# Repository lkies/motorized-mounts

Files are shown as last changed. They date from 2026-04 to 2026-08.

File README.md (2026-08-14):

# DIY Motorized Mirror Mounts

_Lorenz Kies <[lorenz.kies@aei.uni-hannover.de](mailto:lorenz.kies@aei.uni-hannover.de)>_

_I designed this project during my employment as a research assistant at the Institute of Gravitational Physics at Leibniz University Hannover; it is therefore intellectual property of my employer, but I have been given permission to share it under an open source license._

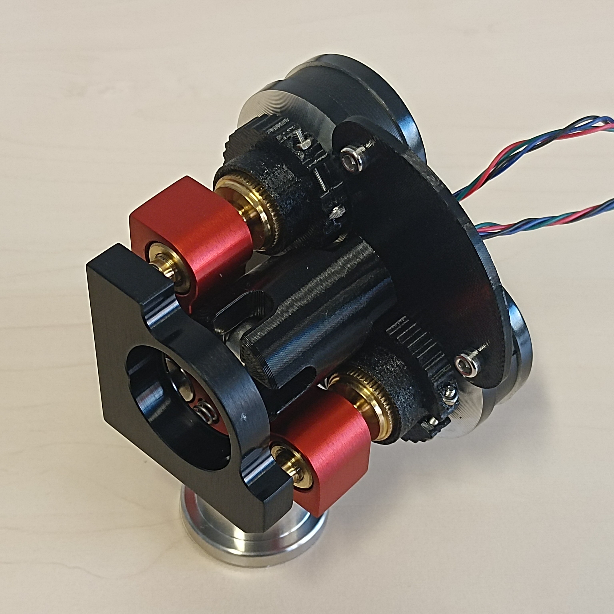
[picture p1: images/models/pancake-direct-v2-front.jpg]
pancake-direct-v2 front view
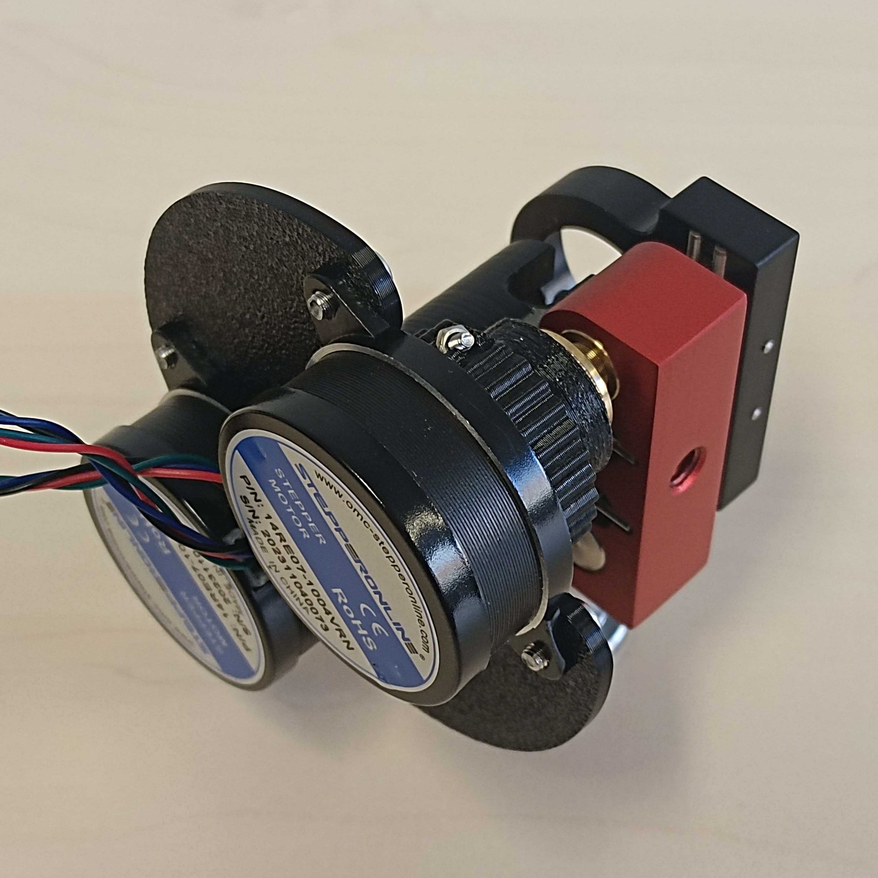
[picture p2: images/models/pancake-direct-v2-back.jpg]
pancake-direct-v2 back view
 

## Introduction

Motorized mirror mounts for guiding laser beams are already an established commercial product, but their pricing makes them unreasonable for basic automation tasks for most people. This means they are mostly reserved for applications where remote control or precise repeatable positioning is required. This is why I decided to develop a low-cost alternative for cheap automatic alignment of optical experiments. Most commercial offerings start at around $1000 per axis (including the driver), or around $4000 for a full 4-axis system required for most alignment problems. In contrast, my design can be build for under $100 for a full set, so less than $25 per axis, relying mostly on standard components and 3D printed parts. Despite the low cost, the actuator performance is competitive with lower-end commercial products and more than sufficient for most automatic alignment problems.

If you want to simply build the actuators, go to the [Instructions](#instructions) chapter. Following that, I discuss some of the [mechanical](#mechanical-design) and [electrical](#electrical-design) design considerations I made, that may be of interest to you, if you want to modify the designs. Finally, I discuss the [characterization](#characterization) experiments and metrics used to evaluate the performance of the actuators.

## Table of Contents

- [Introduction](#introduction)
- [Instructions](#instructions)
  - [Parts List](#parts-list)
  - [Actuator Assembly Instructions](#actuator-assembly-instructions)
  - [Electronics Setup](#electronics-setup)
  - [Firmware Setup](#firmware-setup)
  - [API / Software Setup](#api--software-setup)
- [Design Considerations](#design-considerations)
  - [Mechanical Design](#mechanical-design)
  - [Backlash and Hysteresis Compensation](#backlash-and-hysteresis-compensation)
  - [Electrical Design](#electrical-design)
- [Characterization](#characterization)
  - [Minimal Incremental Motion](#minimal-incremental-motion)
  - [Unidirectional Repeatability](#unidirectional-repeatability)
  - [Nonlinearity](#nonlinearity)
  - [Backlash](#backlash)
  - [Backlash Variation](#backlash-variation)
  - [Interpretation](#interpretation)
  - [Results](#results)

## Instructions

These are the instructions to build the `pancake-direct-v2` design, which is the recommended design. The other designs are mostly included for completeness' sake, if you want to build them you will have to figure it out yourself from the CAD files.

### Parts List

To build a set of **four actuators** on two **mirrors**, you will need the following parts:

| Electronic Parts | Quantity |
| - | - |
| [NEMA 14 Pancake Stepper Motor](https://www.omc-stepperonline.com/de/e-serie-runden-nema-14-bipolar-0-9deg-8ncm-11-33oz-in-1-0a-36x17mm-4-draehte-14re07-1004vrn) | 4 |
| [TMC2208 StepStick V1.2](https://aliexpress.com/item/33045459259.html) | 4 |
| [Makerbase MKS DLC32 MAX](https://aliexpress.com/item/1005008204547315.html) | 1 |
| [19V 5A Power Supply (5.5mm x 2.5mm socket)](https://de.rs-online.com/web/p/steckernetzteile/2552119) | 1 |
| [Cat7 U/FTP 2m Ethernet Cable](https://de.rs-online.com/web/p/ethernetkabel/2660713) (optional) | 2 |
| [Adapter-Board-Stepper](electrical/adapter-board-stepper) (optional) | 2 |
| [Adapter-Board-Controller](electrical/adapter-board-controller) (optional) | 2 |
| [RJ45 Socket](https://de.rs-online.com/web/p/ethernet-steckverbinder/3316443?searchId=30a561ef-d51f-4305-b438-8268e3811f80) (optional, for adapter boards) | 4 |

The links for the motors, motor drivers, and driver board are not affiliate links, they are simply the first results I found. All parts are also offered by many other suppliers. If you can not find the exact same model, you should also be able to use similar parts that perform the same function.

There are a lot of other CNC driver boards out there, many of them ESP32 based. Alternatively, it is also not too difficult to build one yourself. Similarly, you can also use different stepper drivers like the TMC2209, DRV8825 or A4988. Most stepsticks are pin compatible at least to the extent required for basic operations. If you choose to buy TMC2208 stepsticks, I recommend getting the white v1.2 version, there are many step stick designs available and some of them seem to have weird factory side configurations. Although 15V and 3.5A should technically be enough for the power supply, I recommend staying on the safe side and getting a more powerful one like the one specified. If you do not have the capabilities to manufacture PCBs, you can also buy [RJ45](https://de.aliexpress.com/item/1005004520312413.html) breakout boards instead of the custom adapter boards, or skip the Ethernet cables entirely.

| Mechanical Parts | Quantity |
| - | - |
| [MDI-HS Mirror Mount](https://www.radiant-dyes.com/index.php/products/optomechanics/high-stable-mirror-mounts/131-mdi-hs) | 2 |
| DIN 912 M2x16mm | 4 |
| DIN 934 M2 Nuts | 4 |
| DIN 912 M3x6mm | 8 |
| DIN 912 M4x12mm | 4 |
| DIN 912 M6x16mm | 2 |

In most cases, it is not necessary to use DIN 912 of these exact lengths, just use whatever is available.

| 3D Printed Parts | Material | Quantity |
| - | - | - |
| [`gear-grip.stl`](mechanical/pancake-direct-v2/gear-grip.stl) | PETG | 4 |
| [`screw-grip.stl`](mechanical/pancake-direct-v2/screw-grip.stl) | TPU 95A | 4 |
| [`fastener.stl`](mechanical/pancake-direct-v2/fastener.stl) | PETG | 4 |
| [`mount-plate.stl`](mechanical/pancake-direct-v2/mount-plate.stl) | PETG | 2 |
| [`mount-stem.stl`](mechanical/pancake-direct-v2/mount-stem.stl) | PETG | 2 |
| [`adapter-board-mount.stl`](mechanical/adapter-board/adapter-board-mount.stl) (optional) | PETG | 2 |
| [`driver-board-case-lower.stl`](mechanical/driver-board-case/driver-board-case-lower.stl) (optional) | PETG | 1 |
| [`driver-board-case-upper.stl`](mechanical/driver-board-case/driver-board-case-upper.stl) (optional) | PETG | 1 |

Other materials like PLA instead of PETG or other flexible filaments instead of TPU 95A will probably also work, this is just what I used. If you have access to a laser cutter, you can also cut the [`mount-plate.dxf`](mechanical/pancake-direct-v2/mount-plate.dxf) out of 2.5mm to 3mm thick acrylic. This is a bit stiffer and looks nicer.

### Actuator Assembly Instructions

1. Crimp a plug to the wires, make sure that the first two wires are one phase and the second two wires are the other phase, do not mix them. The polarity and positioning of the phases determine the rotation direction, but this does not really matter for most applications.
2. Insert M2 nut into `fastener`. If it does not fit, heat the nut using a lighter or soldering iron. If it does not sit tight, heat the plastic and press it together around the nut. Alternatively, hose clamps might also work well for this, but I did not test that.
3. Put the `gear-grip` on the output gear of the motor. If it is too tight, slightly bend the two halves apart. The part has a chamfer on one side that should also help with this.
4. Put the `screw-grip` on the `gear-grip`, make sure that the shallow slots in the `gear-grip` align with the shallow notches on the `screw-grip`.
5. Push the `fastener` onto the `gear-grip`, if it is too tight, slightly bend the `fastener` apart. The `fastener` has a chamfer that should mate with a very thin shoulder on the `screw-grip` to help with the alignment.
6. Before tightening the fastener, use a knife (or another thin piece of metal) to make a small gap (~0.5mm) between the motor and `gear-grip` to avoid unnecessary friction between the two.
7. Tighten the fastener using an M2x16mm screw. If the M2 nut in the `fastener` breaks free, use pliers to hold it in place while tightening.
8. Repeat steps 1-7 for the other three motors.
9. Fasten the `mount-plate` to the `mount-stem` using two M4x12mm screws. Repeat for the other mount.
10. Place two motor assemblies on their back with the wires facing inwards. (Not really necessary, but it looks nicer in my opinion.)
11. Fasten the `mount-plate` / `mount-stem` assembly onto the two motors using four M3x6mm screws. Repeat for the other mount.
12. Put a M5x16mm screw through the hole of the mirror mount that is **not** used for screwing it to its foot. Screw it in so that the head is roughly in the center of the optical axis.
13. Place the whole mirror actuator assembly onto the mirror mount and tighten the M5 screw. Repeat for the other mount. When setting up the mounts as part of a setup, I recommend doing the placement and rough alignment without the actuator assembly attached, and only attaching it for fine automatic alignment.

Instructions

### Electronics Setup

1. For each of the red DIP switches between the stepstick slots, switch them all to the down/off position to select 8 microsteps per full step.
2. Plug the stepsticks into the driver board. Most stepsticks have some of the pins labeled _somewhere_ so you know which way around to plug them in.
3. If you built the adapter boards, plug them in. Beware, many CNC driver boards have two sockets for the y-axis, make sure to skip the second one.
4. **With the motors disconnected**, connect the power supply and adjust driver current reference voltage as described in the ["Motor Current Setting"](https://wiki.fysetc.com/docs/TMC2208#Motor%20Current%20Setting) section. I set it to 800 mV which indicates an RMS current of 800 mA. This may be slightly different for other stepstick designs. The drive current is a tradeoff between torque and heating. With a larger current, the motor can produce more torque and consequently move at higher speeds. However, it will also heat up faster and reach higher temperatures. The TMC2208 has an auto power-down feature that reduces the current during standstill. If you have this feature and use the motors infrequently enough, you may get away with higher currents without overheating. The motors are rated for 1.0 A per phase, so with 800 mA, should be on the safe side.
5. Attach the driver board adapters to the driver board and put the assembly in the case and close it with six DIN 912 M3x20 screws.

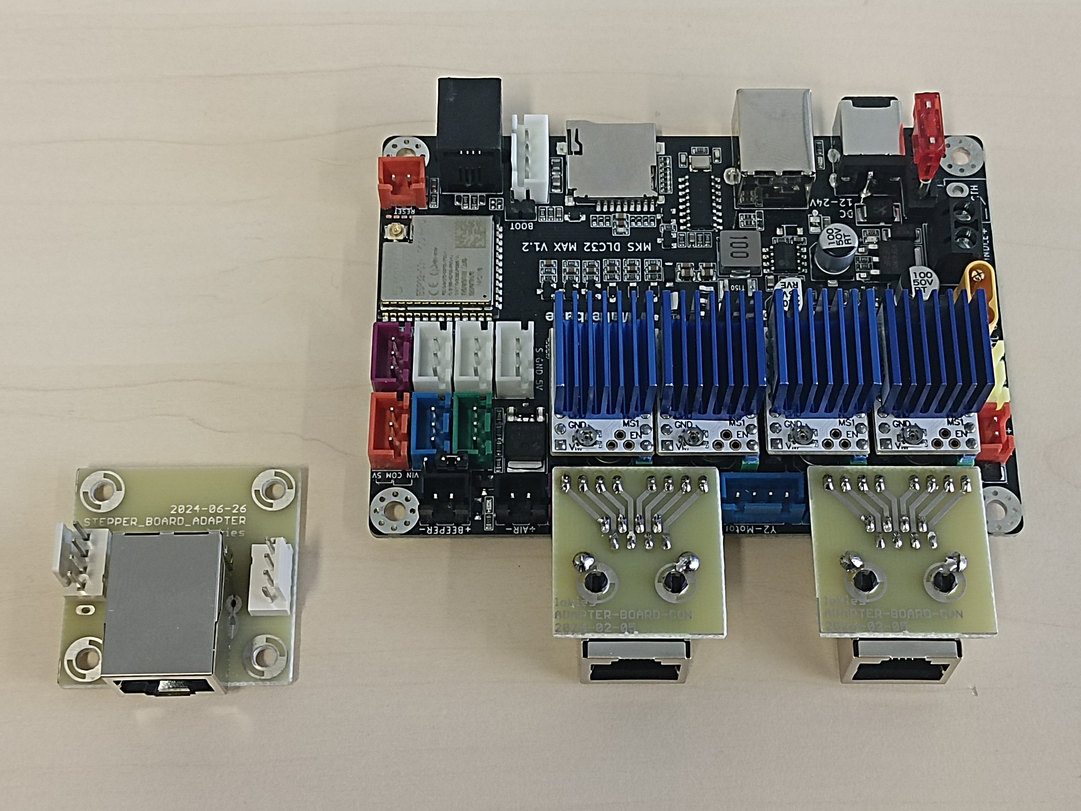
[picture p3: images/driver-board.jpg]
Driver Board
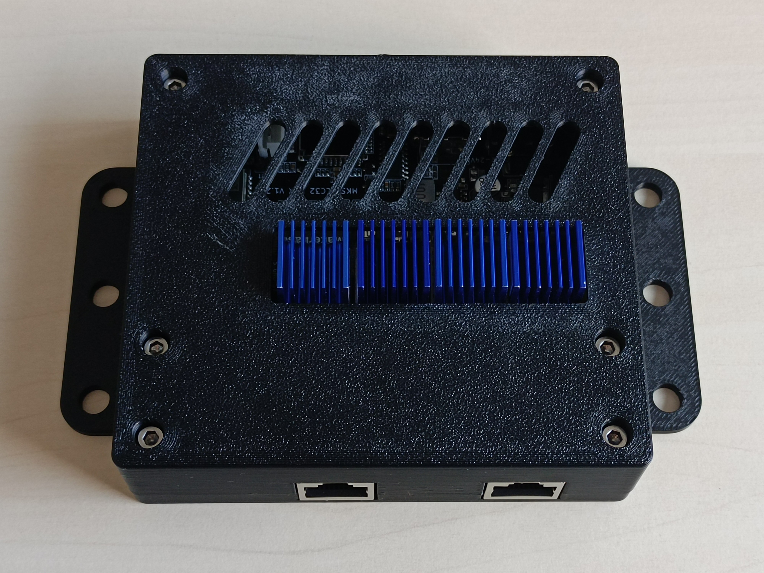
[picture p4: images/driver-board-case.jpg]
Driver Board Case
 

### Firmware Setup

1. Install Python in your preferred way.
2. Install [`esptool`](https://pypi.org/project/esptool/) for example using pip:

    ```shell
    pip install esptool
    ```

3. Download the [firmware image](firmware/firmware.bin).
4. Erase the flash memory of the controller board using:

    ```shell
    esptool --chip esp32s3 erase_flash
    ```

    If you have multiple serial devices connected, you may also need to specify the port using `--port COM[X]` on Windows or `--port /dev/ttyUSB[X]` on Linux.

5. Flash the image using:

    ```shell
    esptool --chip esp32s3 write_flash 0x0 firmware.bin
    ```

    The same note about the port applies here as well.

If you are using a different board, you will need to configure the correct pins and potentially switch the build system different architecture. You can find more details on this in the [`firmware` directory](firmware).

### API / Software Setup

1. Install Python in your preferred way.
2. Install the API package from source control using pip:

    ```shell
    pip install git+https://github.com/lkies/motorized-mounts.git#subdirectory=api
    ```

3. Control the steppers through a `StepperBoard` instance:

    ```python
    from stepper_board import StepperBoard, RpcClient, SerialBLS

    # the default baudrate of ESPs is 115200
    with SerialBLS.connect("COM[X]", 115200) as bls:
        # create proxy instance of stepper board connected to serial port
        steppers = StepperBoard(RpcClient(bls))

        # configure speed, acceleration and compensation settings
        # only needed once, the settings are saved the board's non-volatile memory
        for i in range(4):
            steppers.set_max_speed(i, 500)
            steppers.set_max_accel(i, 1e5)
            steppers.set_backlash(i, 10) # in case you want to use backlash compensation
            steppers.set_hysteresis(i, 30)
            steppers.set_compensation("hysteresis")

        # enables the stepsticks
        steppers.set_enabled(True)

        # move stepper 0 to position 1000 microsteps
        steppers.move_to(0, 1000)

        # move multiple steppers simultaneously
        steppers.move_to_vec([10, 20, 30, 40], "joint_max") 
    ```

The configuration only needs to be done once, the settings are stored on the chip's non-volatile memory and it is automatically reloaded at startup. From the characterization measurements, the backlash compensation should be about 10 microsteps at 8 microsteps per full step. The hysteresis compensation needs to be at least as large as the maximum backlash, in this case, greater than about 15 microsteps. To be on the safe side, we choose 30 microsteps. A larger hysteresis correction will cause more unnecessary extra movement, but at these small scales, it does not really matter. The best performance is achieved with hysteresis compensation, so unless you have a good reason to use backlash compensation, I would recommend using hysteresis compensation.

You can find more information about the driver boards behavior in the [`api` directory](api).

_Please consider providing feedback on the build process if you end up replicating this design so that we can optimize the instructions and the design itself. Have Fun!_

## Design Considerations

### Mechanical Design

Building a stable and robust mirror mount is not a trivial task. That is why I did not do it and instead built the design around the [MDI-HS](https://www.radiant-dyes.com/index.php/products/optomechanics/high-stable-mirror-mounts/131-mdi-hs) series mirror mounts from Radiant Dyes. They have proven themselves as reliable and stable mirror mounts in our labs. They also have slightly larger thumbscrews than other mounts, which is helpful in reducing coupling slack between them and the motor.

For the motors, I experimented with two different types of stepper motors: the extremely cheap 28BYJ-48 geared stepper motors and the slightly more expensive [Nema 14 Pancake motors](https://www.omc-stepperonline.com/de/e-serie-runden-nema-14-bipolar-0-9deg-8ncm-11-33oz-in-1-0a-36x17mm-4-draehte-14re07-1004vrn) (400 step/rev version). The 28BYJ-48 motors are normally unipolar stepper motors, but they are not too difficult to [modify for bipolar operations](https://ardufocus.com/howto/28byj-48-bipolar-hw-mod/). This has two advantages: first, bipolar operation is not limited to using half the coil windings, which means more torque. Second, and much more importantly, it is much easier to get good microstepping drivers for bipolar motors, such as the TMC2208. This is very important because the excess vibration caused by bad drivers causes a lot of problems with sensitive optical experiments.

One simple method for increasing the actuation resolution of an actuator is to use a gear reduction. However, this may not always lead to better performance since the gearing also introduces backlash and other hysteresis-like effects. To investigate this, I designed a geared and a direct drive version for both motors. Typically, gearboxes, especially stiff metal gears, are intentionally designed with some slack to prevent jamming and allow for lubrication, but this also means that they will have backlash. Without this play, even tiny manufacturing tolerances can reduce the slack "below zero" which then requires strong deformation forces to move past, if possible at all. This is not as critical in plastic gears, which allow for more deformation. In fact, we can deliberately introduce radial compliance in the gear, which then allows us to preload them without the risk of jamming and excessive required forces to move. With this, we can effectively eliminate backlash, but the compliance itself may introduce other hysteresis-like effects.

Another challenge is to provide a reliable coupling between the motor and the mount. While a form fit is generally good for preventing slippage, it requires precise manufacturing to match the mating part. In addition to that, the stiff coupling requires the axis of the mount to be very well aligned with the axis of the motor, otherwise the mechanism may not be able to move freely. Because of these reasons, I choose to use a friction fit with TPU 95A, providing the required compliance. This has a few advantages, firstly, the compliance allows for slight radial misalignments by deforming. The knurled knob provides good grip for torque transfer while still allowing for some axial slip to deal with the screw moving in and out of the mount as it is actuated. And finally, it is easy to manufacture on most 3D printers and does not require additional elements like grub screws. The major disadvantage is that there will be additional hysteresis-like effects. In practice, this does not seem to be very severe, although it is possible that it is currently a limiting factor on the minimal incremental motion.

### Backlash and Hysteresis Compensation

While there is only one way for an actuator to be "perfect", i.e. a simple linear mapping from desired position to actual mirror orientation, there are many ways in which an actuator can be imperfect. Here is a list of the types of imperfections investigated and possible compensation approaches. You can find more details about how we characterized them in the [Characterization](#characterization) section.

- Minimal Incremental Motion: This is the smallest unidirectional change in position that the actuator can reliably produce. Changes in input that are smaller have no meaningful effect on the output due to digital resolution limits, stick-slip effects or limitations in the drive train.
- Backlash: It is commonly defined as "the maximum distance or angle through which any part of a mechanical system may be moved in one direction without applying appreciable force or motion to the next part in mechanical sequence." For our purposes, we can define it as the additional change in input we need to apply after a direction change before the output starts to change. If this is consistent, it can be compensated for by adding that amount to the input when changing direction.
- Backlash Variability: If the backlash is not consistent over the actuator's range of movement, it can not be compensated for with simple backlash compensation. However, if it is consistent for a given position, we can compensate for it by always approaching the desired position from the same direction. With this approach, we can also compensate for any other hysteresis-like effects, so we will call it hysteresis compensation as opposed to the simple backlash compensation. Hysteresis compensation is generally more robust and leads to better accuracy because it compensates for more imperfections and does not require precise knowledge of the backlash. However, it is slower since it requires extra movement to approach the desired position from the correct direction.
- Macroscopic Nonlinearity: Besides the small-scale nonlinear behavior described by the minimal incremental motion, there may also be macroscopic nonlinearities due to non-ideal components in later stages of the transmission. These could be compensated for by calibrating them out, but this is generally not necessary for automatic alignment applications where precise repeatable movement is much more critical.

### Electrical Design

The stepper motors are a crucial part for providing precise, repeatable actuation. To get the best performance out of them, it is important to use good stepper drivers. I chose the TMC2208 drivers because of their quiet and vibration free stealth chop mode to avoid disturbing sensitive optical experiments, but other drivers might also be good enough and are usually pin compatible if integrated onto a stepstick. To drive them I used an ESP32 (old or S-series) because of their high resolution timers and established ecosystem. While it is not too hard to design a PCB that connects the microcontroller to the four stepsticks, it is superfluous because this kind of problem has been solved many times before for CNC machines, 3D printers and laser cutters. There are a lot of these boards out there, and quite a few of them even use the ESP32 based controllers. I selected the Makerbase MKS DLC32 MAX V1.2 because it is compact and cheap (<20€ on AliExpress) and has the required four stepper driver slots and ESP32s3 controller. Sadly, the schematics are not open source, but the [pinout](https://github.com/user-attachments/files/19184922/MKS.DLC32.MAX.V1.0_002.PIN.pdf) can be found online.

I wrote my own firmware that implements speed and acceleration limits, as well as backlash and hysteresis compensation, with a simple JSON-based serial interface to control it. But it might be interesting to investigate using established software like [GRBL](https://github.com/grbl/grbl) to simplify the project even further.

While the motors I used do not require much power, I would still recommend using a power supply with more than 15V. At high speeds, the inductance becomes the limiting factor in how much current can flow. If the driver has a higher voltage supply, it can change the current through the inductor faster to maintain reasonable torque at high speeds. But be careful setting the current limit on the drivers, they can easily overheat and potentially damage the 3D printed parts.

Since you will most likely not want to mount the controller board on your optical table, you will need to extend the motor wires somehow. For this, I recommend using Ethernet cables. With four twisted pairs, a single Ethernet cable can drive two stepper motors, enough for the two axes of a single steering mirror. Another advantage of using Ethernet cables is that they also shield the individual motor wire pairs preventing electromagnetic interference from the comparatively high drive currents. While more shielding might sound attractive, especially considering the current going through these wires, I still recommend using U/FTP cables because they are typically much more flexible than cables with overall shielding. To go from the driver board to RJ45 and back at the mirrors, we use custom adapter boards, but you can also buy RJ45 breakout boards if you do not have the capability to make your own.

## Characterization

To measure the performance of the actuators, we use one simple experiment and multiple evaluations to extract the quantities of interest from the data. The experimental setup is very straightforward, we shine a laser beam at the mirror of the mount to be evaluated and then measure the changes in position on a screen. The position which is approximately proportional to the change in mirror angle is measured using the difference voltage of a four quadrant photodetector, while this is not linear in the position, the nonlinearity is easy to calibrate out. We then move the actuator back and forth multiple times and record the input and measured output position. After each movement, we wait for 100 ms for the mount and table to settle to get as precise a measurement as possible. All performance metrics are then derived from this data.

Example code for computing the quantities can be found in the [plotting notebook](images/plots/plots.ipynb). The actual code used is slightly different and can be found in the [evaluation module](characterization/evaluation.py). To better illustrate the individual effects, the example plots shown are based on simulated data which is also generated in the plotting notebook.

### Minimal Incremental Motion

In a loose sense, the minimal incremental motion is the smallest change in input, that reproducibly leads to a change in output. To quantify it we look at small segments of the unidirectional travel, where other nonlinearities are negligible. We compute the mean expected movement using a unity slope linear regression line and then look at the distribution of the residuals. Ideally, the span of the distribution i.e. max - min then gives us the minimal change in input that we need to apply to get a reliable change in output. In practice, the measurements are subject to noise and so maximum and minimum values are most likely outliers which are not representative of the expected performance. We can mitigate this by only looking at the inner $x$ percent of values. For example if we want to take the inner 95% of values we use the 2.5th and 97.5th percentile instead of the minimum and maximum.

We can get estimates of the confidence intervals by bootstrapping the distribution of residuals.

<image src="images/plots/min_increment.png" alt="Minimal Incremental Motion Plot" width="400px"/>

The plot shows minimal incremental motion limited by stick slip effects. For most small changes in input, the system "sticks" and the changes in output are purely noise. Once the input change is large enough, the system "slips" and the output changes suddenly. Because of this, the system can not be controlled at scales finer then the "steps" of the slips.

### Unidirectional Repeatability

In addition to the mostly consistent stick-slip effects that limit the minimal incremental motion, there may be other randomized effects that cause the actuator's output to differ between multiple repetitions of the same input. We call this unidirectional repeatability. This is in contrast to bidirectional repeatability, which is usually limited by backlash and backlash variation. We determine it by examining the peak-to-peak deviation in output across multiple repetitions of the same input, while accounting for movement direction. And again, to account for measurement noise, we do not use the maximum and minimum values but instead use percentiles for greater robustness against noise and outliers. By only comparing against points with the same input and direction as opposed to a linear regression line, this metric is independent of nonlinearity or backlash.

<image src="images/plots/unidirectional_repeatability.png" alt="Unidirectional Repeatability Plot" width="400px"/>

Moving through the same segment multiple times, we see that the output randomly ends up in slightly different positions, limiting the achievable accuracy.

### Nonlinearity

Ideally, after accounting for backlash and minimal incremental motion, there should be a linear relationship between input and output position. In practice, this might not be the case due to manufacturing tolerances across various parts of the drive train. To quantify this, we look at motion across a large segment of the travel and compute the residuals to a linear regression. Similar to minimal incremental motion, instead of directly using the minimum and maximum values, we use percentiles to mitigate the effects of outliers.

<image src="images/plots/nonlinearity.png" alt="Nonlinearity Plot" width="400px"/>

The input-output relationship is not perfectly linear. A user or application that assumes linear behavior will see a systematic deviation from the expected output corresponding to the nonlinearity.

### Backlash

In general, hysteresis is the dependence of a system's state on its history. In the context of actuators, this usually means whether we previously moved the actuator in the same direction or not. In more complicated cases, the behavior may also depend on how long ago the last change in direction was. The dominant source of hysteresis effects in mechanical systems is usually backlash. It is the consequence of play in the force-transmitting elements of the actuator. When we change direction, parts with play need to move through a dead zone before they make contact again and start transmitting force. We defined backlash as the additional movement we need to apply to the actuator after changing direction before the output begins to change.

To determine the backlash from measured data, we can perform a virtual backlash compensation during measurement post-processing. For this, we split all movement segments into forward and backward motion. Then we then shift the recorded input values of the backwards motion by the amount of backlash to compensate for. Finally, we delete the datapoints in the dead zone after changes in direction. We define the backlash as the compensation value that maximizes overlap between the forward and backward segments. In the process, we also get backlash-compensated data that we can use for other evaluations.

Alternatively, we can also determine the backlash as the negative of the signed integral of the hysteresis loop in the input-output space relative to the maximum change in output position (i.e. change in input minus backlash). The advantage of this method is that it does not require a metric to compute the overlap between forward and backward segments. The downside is that we always need to integrate over full hysteresis loops to get valid results. Additionally, we also do not get backlash compensated data for other evaluations.

In both of these evaluations, we compute the backlash in terms of the input position. However, we are usually interested in the backlash in terms of output position. For this, we just multiply it by the input-output proportionality.

It is important to note that it is a matter of convention that we choose the forward direction to be the true direction and the backward direction to be the one affected by backlash. We could just as easily select the backward direction to be the true direction or any mix of the two and split the backlash compensation between the two. However, there is an output offset between the different conventions. The driver board considers the forward direction to be the true direction and applies the backlash compensation to the backward direction, so we stick to this convention for consistency.

We can get confidence intervals by computing the backlash for each cycle individually and then using standard t-statistic-based confidence intervals.

<image src="images/plots/backlash.png" alt="Backlash Plot" width="400px"/>
When changing direction, there is a dead zone before the output starts to change again. This means that the output position is consistently to hight when moving backwards. By shifting the recorded input values for all backwards motion and cutting out the dead zone after direction changes, the forward and backward trajectories overlap again.

### Backlash Variation

While constant backlash is not too difficult to compensate for by adding a constant bias after a direction change, this does not work for variable backlash. In that case, compensating for an average backlash will lead to overcompensation in some cases and undercompensation in others. Quantifying this is somewhat messier than the other metrics, as we need a way to determine the local backlash. To get a reasonable estimate of the local backlash, we need to be able to determine the input deviation between the forward and backwards trajectories for the same output positions. To provide a balance between resolution and smoothing, we interpolate using a Gaussian kernel with a bandwidth equal to the average spacing between consecutive outputs. We then collect all deviations between forward and interpolated backwards or backwards and interpolated forward trajectories. From these deviations we can then again compute lower and upper quantiles to get noise-robust estimates of the differences between maximum and minimum values.

<image src="images/plots/backlash_variation.png" alt="Backlash Variation Plot" width="400px"/>

The backlash is not consistent across the range of movement. After compensating for the average backlash, the range with small backlash is overcompensated and the range with large backlash is undercompensated. This leads to a systematic deviation from the expected output that depends on the position of the actuator.

### Interpretation

An obvious question that arises when looking at these metrics and comparing different motors is, which of these metrics actually matter? The annoying answer here is, it depends on the application and the compensation mode or lack thereof, that is used. For this, we need to introduce the terms of accuracy and precision, which we will call repeatability, to avoid confusion with accuracy. Accuracy describes the deviation of the _expected_ output (i.e., averaged across many iterations) from the true (linear) relation, or, in a looser sense, whether the average output is correct. Precision or repeatability describes the deviation of individual measurements between multiple repetitions of the same input, or in a looser sense, is the actuator consistent. So accuracy or lack thereof is a matter of systematic errors, while repeatability is a matter of random errors. Even though backlash and backlash variation are technically deterministic, we will treat them as random errors for measures of repeatability, as they can appear random to a user or algorithm that is not aware of the history of the actuator.

With this, we can specify the expected performance for different compensation modes. The specified values are bounds for worst-case deviations, discounting errors from noisy measurements and extreme outliers (because we used percentiles instead of maximum and minimum values). We assume that the backlash compensation is applied with the median backlash (between minimum and maximum variation) and that the hysteresis compensation is applied with at least the maximum backlash.

| Compensation Mode       | Remaining (In-)Accuracy                      | Remaining (Un-)Repeatability                                                              |
|-------------------------|----------------------------------------------|-------------------------------------------------------------------------------------------|
| None                    | Backlash + Backlash Variation + Nonlinearity | Backlash + Backlash Variation + Unidirectional Repeatability + Minimal Incremental Motion |
| Backlash Compensation   | Backlash Variation + Nonlinearity            | Backlash Variation + Unidirectional Repeatability + Minimal Incremental Motion            |
| Hysteresis Compensation | Nonlinearity                                 | Unidirectional Repeatability + Minimal Incremental Motion                                 |

If we define the ground truth to lie between the most extreme positive and negative deviations, the actual accuracy and repeatability will be half the values specified.

Depending on the application, either the accuracy or repeatability may be more important. For example, for auto-alignment applications using hysteresis compensation, the nonlinearity will effectively distort the observed figure of merit in terms of the input. As long as this distortion is small enough, this should not matter to the optimizer which mostly cares about repeatability.

Overall, the best performance is achieved with hysteresis compensation, and it should therefore be the default choice for most applications. The only downside compared to backlash compensation is that it leads to additional movement to always approach the desired position from the same side. This makes actuation slower, especially if most movements are smaller than the hysteresis compensation value.

### Results

At the time of performing the characterization measurements, we also had two commercial models from Newport available, which they had kindly lent us for evaluation. The [TRA6CC](https://www.newport.com/p/TRA6CC) designated as `newport-dc` is a closed loop DC motor, the [TRA6PPD](https://www.newport.com/p/TRA6PPD) designated as `newport-stepper` is an open loop stepper motor based design.

The characterization experiments were performed with the following parameters:

- Short evaluation range: $5\text{ mdeg}$ (Used for minimal incremental motion)
- Long evaluation range: $50\text{ mdeg}$ (Used for all other evaluations)
- Number of cycles for short stroke high resolution measurements: $10$
- Number of cycles for long stroke measurements: $5$
- Evaluation quantile for noise robust min max estimates: $95\%$ (i.e. 2.5th and 97.5th percentiles)
- Confidence interval: $95\%$ (rounded up to larger deviation for asymmetric intervals)
- Bootstrap samples: $10 000$

The actual stroke lengths varied between the different motors, but they were all larger than the evaluation range.

| Actuator Model    | 95% min. inc (µdeg)   | 95% uni. rep. (µdeg)   | 95% nonlin. (µdeg)   | backlash (µdeg)   | 95% BL var. (µdeg)   |
|:------------------|----------------------:|-----------------------:|---------------------:|------------------:|---------------------:|
| `cheap-geared`    | 521 ± 27              | 490 ± 19               | 1034 ± 23            | 2763 ± 116        | 507 ± 19             |
| `cheap-direct`    | 490 ± 39              | 2014 ± 131             | 923 ± 44             | 4420 ± 590        | 2007 ± 132           |
| `pancake-geared`  | 445 ± 18              | 1144 ± 25              | 803 ± 40             | 1620 ± 768        | 1154 ± 20            |
| `pancake-direct`  | 503 ± 33              | 614 ± 21               | 613 ± 20             | 1543 ± 170        | 622 ± 20             |
| `newport-dc`      | 285 ± 15              | 534 ± 18               | 587 ± 18             | 10692 ± 105       | 539 ± 17             |
| `newport-stepper` | 298 ± 16              | 441 ± 17               | 533 ± 16             | 10049 ± 63        | 459 ± 14             |

The uncertainty estimates provided are purely derived from statistical data and do therefore not account for systematic errors. For example, the `cheap-direct` instance was probably built using an unusually bad motor since it has significantly more backlash variation and repeatability than the geared version. Even with a perfect gear reduction, the direct-drive version should only be three times as bad as the geared version.

It is interesting to note that all DIY designs have roughly the same minimal incremental motion. This suggests that it is not limited by the motor or gear reduction but rather by the parts they share in common. The most likely candidate for this is the TPU friction fit coupling, but it is also possible that it is the threading in the mirror mount. To put this into context, $500\text{ µdeg}$ in rotation corresponds to about $270\text{ nm}$ of screw translation, which is already impressively small for something based on metal sliding on metal.

Overall, the `pancake-direct` design has the best overall performance of the DIY designs, while also being the simplest to build. It is still beaten by the commercial models in terms of minimal incremental motion, but it has very similar performance in terms of repeatability, nonlinearity and backlash variation. The backlash itself is significantly better than the commercial models, although this does not necessarily provide an advantage in practice since backlash is easily compensated. However, it does make hysteresis compensation more feasible since the extra movement required to approach the desired position from the correct direction is smaller. It is worth noting that the Newport motors were at a slight advantage due to their larger mirror mount lever of $40\text{ mm}$ compared to $31\text{ mm}$ for the DIY designs.

If more accurate actuation is required, the Radiant Dyes mirror mounts are also available with $100\text{ µm/rev}$ screw pitch as opposed to the $250\text{ µm/rev}$ used here. Depending on what the limiting factors are, this might provide **up to** a 2.5-fold reduction in all metrics, leading to minimal incremental motions around $200\text{ µdeg}$.

There are also notable differences between the DIY and commercial models that these metrics do not capture. Most importantly, the commercial models have homing capabilities while the DIY motors do not. However, for automatic alignment applications, which was the main motivation for building these motors, the loop is closed by the figure of merit, and homing is therefore not really necessary and more of a convenience feature. Another advantage of the commercial models is that they move faster, although we made no comprehensive quantitative measurements to compare this in detail. On the other hand, the DIY motors have two important practical advantages. First, they can easily be attached to existing mounts without changing their position. This also means they can easily be removed for manual prealignment which is much more convenient than having to steer them through control software on a computer. Secondly, they are much more compact, which makes the mirrors they are attached to easier to handle and also allows for placement in much tighter places.

And finally, they are of course **much** cheaper with less than 3% of the cost of commercial models.

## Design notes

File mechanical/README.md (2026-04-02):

# Mechanical Designs for Motorized Mounts

This directory contains the CAD files for the mirror actuators. For completeness’ sake the four original designs are included here, but **it is recommended that you use the [`pancake-direct-v2`](pancake-direct-v2) design**.

## Designs

The available designs are:

- [`cheap-geared`](cheap-geared): Geared design using the 28BYJ48 "cheap stepper" motors with 1:3 gear reduction.
- [`cheap-direct`](cheap-direct): Direct drive design using the 28BYJ48 "cheap stepper" motors.
- [`pancake-geared`](pancake-geared): Geared design using the NEMA 14 "pancake" stepper motors with 1:3 gear reduction.
- [`pancake-direct`](pancake-direct): Direct drive design using the NEMA 14 "pancake" stepper motors.
- [**`pancake-direct-v2`**](pancake-direct-v2): Similar design to `pancake-direct` but optimized for easier printing and assembly.

<br>

Mount Models

## Transmission Ratios

When using the driver board, we specify the desired position in terms of microsteps, even though what we really care about is the angle of the mirror. The final ratio $r$ between microsteps and mirror angle is the result of the proportionalities of all the individual parts:

$$r = r_d \cdot r_m \cdot r_g \cdot r_s \cdot r_l$$

Where:

- $r_d$ (unitless) is driver ratio or microstep setting, i.e., the number of full steps per pulse of the step pin.
- $r_m$ (unitless) is the motor ratio, i.e., the number of full steps per revolution of the motor shaft.
- $r_g$ (unitless) is the gear ratio, i.e., the number of revolutions of the adjustment screw per revolution of the motor shaft.
- $r_s$ (in $\text{m}$) is the screw pitch, i.e., the screw translation for one revolution.
- $r_l$ (in $\text{deg/m}$) is the lever ratio, i.e., the mirror rotation per unit of screw translation.

The values for these ratios for the different designs are as follows.

| Design | $r$ ($\text{µdeg/microstep}$) | $r_d$ | $r_m$ | $r_g$ | $r_s$ ($\text{µm}$) | $r_l$ ($\text{deg/mm}$) |
| - | - | - | - | - | - | - |
| `cheap-geared` | ~9.40 | 1/8 | 1/2048 | 1/3 | 250 |  ~1.85 |
| `cheap-direct` | ~28.2 | 1/8 | 1/2048 | 1 | 250 |  ~1.85 |
| `pancake-geared` | ~48.1 | 1/8 | 1/400 | 1/3 | 250 |  ~1.85 |
| `pancake-direct` | ~144 | 1/8 | 1/400 | 1 | 250 |  ~1.85 |

The microstep setting can easily be changed, but I kept it at 8 microsteps per full step. The mirror mounts used have a thread pitch of $250\text{ µm/rev}$, and the lever length of the mirror is also always $31\text{ mm}$. The motor ratio for the cheap stepper may depend on your model, some have a slightly different gearing, which differs by half a percent.

It is important to note that these numbers by themselves make no statement about the performance of the different designs. At best, they are an upper limit on the resolution, however, it is not of much consequence.

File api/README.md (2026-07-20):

# Stepper Driver Board API

The driver board is controlled via a minimalistic JSON based remote procedure call (RPC) protocol.

You can install the package directly from this repository using PIP:

```bash
pip install git+https://github.com/lkies/motorized-mounts.git#subdirectory=api
```

The full API documentation for the stepper driver board is described in the [`stepper_board`](doc/stepper_board.md) module documentation. The RPC internals are described in the [`rpc`](doc/rpc.md) module. The [`serial_socket`](doc/serial_socket.md) module provides a simple bridge between serial and TCP connections.

## Connecting to the Board

The board is controlled through a [`StepperBoard`](doc/stepper_board.md#stepper_board.StepperBoard) instance. These need to be initialized with an [`RpcClient`](doc/rpc.md#rpc.RpcClient), which in turn needs to be initialized with a transport, like a [`SerialBLS`](doc/rpc.md#rpc.SerialBLS) or a [`SocketBLS`](doc/rpc.md#rpc.SocketBLS) instance. Since the board uses serial, we use a [`SerialBLS`](doc/rpc.md#rpc.SerialBLS):

```python
from stepper_board import StepperBoard, RpcClient, SerialBLS

bls = SerialBLS.connect("COM3", 115200)
steppers = StepperBoard(RpcClient(bls))
# do stuff with the steppers...
bls.close()
```

The [`SerialBLS`](doc/rpc.md#rpc.SerialBLS) (and other classes inheriting from [`BidirectionalLineStream`](doc/rpc.md#rpc.BidirectionalLineStream)) can also be used as a context manager to automatically close the wrapped serial port (or other resource) when done:

```python
with SerialBLS.connect("COM3", 115200) as bls:
    steppers = StepperBoard(RpcClient(bls))
    # do stuff with the steppers...
```

It is also possible to connect to the board via TCP using the [`SocketBLS`](doc/rpc.md#rpc.SocketBLS) class. For this, the serial port needs to be exposed as a TCP socket first. This can be done with tools like [ser2net](https://github.com/cminyard/ser2net) or the provided [`serial_socket`](doc/serial_socket.md) module.

```bash
python -m stepper_board.serial_socket COM3 --baudrate 115200 --host 127.0.0.1 --port 7000
```

The baud rate, host, and port are optional and default to the values shown in the example. Once the port is exposed, it can be connected in almost the same way as directly connecting to a serial port but using a [`SocketBLS`](doc/rpc.md#rpc.SocketBLS) instead of a [`SerialBLS`](doc/rpc.md#rpc.SerialBLS):

```python
with SocketBLS.connect("127.0.0.1", 7000) as bls:
    steppers = StepperBoard(RpcClient(bls))
    # do stuff with the steppers...
```

## Enabling the Stepper Drivers

The stepsticks plugged into the board all have an enable pin, which can be controlled with the [`set_enabled(enabled)`](doc/stepper_board.md#stepper_board.StepperBoard.set_enabled) method. When disabled, the drivers will not output any current through the motors. Conversely, if they are enabled, even if they are not moving, the drivers will still output the full current (or a reduced current if they have a power-down feature like the TMC2208s) to hold the motor in place. To prevent excessive heating of the motors and drivers and lengthen their lifespan, it is therefore recommended to shut them off when they are not needed.

To prevent accidental damage to the motors due to bad driver settings and overheating, the driver board will automatically disable the drivers after receiving no command for some time, the default is 300 seconds. The timeout can be changed with the [`set_timeout(timeout)`](doc/stepper_board.md#stepper_board.StepperBoard.set_timeout) method or disabled entirely by setting the timeout to zero. The current timeout and whether the steppers are enabled can be queried with the [`timeout()`](doc/stepper_board.md#stepper_board.StepperBoard.timeout) and [`enabled()`](doc/stepper_board.md#stepper_board.StepperBoard.enabled) methods.

When the motors are disabled, the driver board will store the current position of the steppers to non-volatile memory so the steppers do not lose their position when turned off.

## Movement Commands

There are multiple movement commands available to set the steppers position.

The simplest one is [`move_to(index, position, speed=MAX_SPEED)`](doc/stepper_board.md#stepper_board.StepperBoard.move_to), which moves a single stepper to a specific position in microsteps. As an optional third parameter, you can specify the speed in units of microsteps per second. If the speed is not specified or set larger than the allowed maximum speed, the stepper will move at its configured maximum speed.

To move multiple steppers at the same time, you can use the [`move_to_vec(positions, speed_mode, speed=MAX_SPEED)`](doc/stepper_board.md#stepper_board.StepperBoard.move_to_vec) method. The positions must be a list of the desired positions in microsteps. If fewer than four positions are specified, the remaining positions will be set to zero. The available speed modes are:

- `"individual_max"`: Each stepper moves at its own maximum speed.
- `"joint_max"`: The speeds of the steppers are adjusted so that they all finish at the same time, the speed is determined by the maximum speed of the stepper that takes the longest time to reach its target.
- `"joint_euclid"`: The speeds of the steppers are adjusted so that they all finish at the same time, the euclidean norm of the speeds must be specified in the `speed` parameter.
- `"joint_cheby"`: The speeds of the steppers are adjusted so that they all finish at the same time, the chebyshev norm (max of the absolute values) of the speeds must be specified in the `speed` parameter.

Both of these functions are blocking, i.e., they will only return once the steppers have reached their target positions.

Alternatively, the movement can be controlled asynchronously using the [`set_target(...)`](doc/stepper_board.md#stepper_board.StepperBoard.set_target) and [`set_target_vec(...)`](doc/stepper_board.md#stepper_board.StepperBoard.set_target_vec) functions in combination with [`wait(...)`](doc/stepper_board.md#stepper_board.StepperBoard.wait), [`wait_vec()`](doc/stepper_board.md#stepper_board.StepperBoard.wait_vec), [`stop(...)`](doc/stepper_board.md#stepper_board.StepperBoard.stop), [`stop_vec()`](doc/stepper_board.md#stepper_board.StepperBoard.stop_vec), [`steps_remaining(...)`](doc/stepper_board.md#stepper_board.StepperBoard.steps_remaining) [`steps_remaining_vec()`](doc/stepper_board.md#stepper_board.StepperBoard.steps_remaining_vec), [`time_remaining(...)`](doc/stepper_board.md#stepper_board.StepperBoard.time_remaining) and [`time_remaining_vec()`](doc/stepper_board.md#stepper_board.StepperBoard.time_remaining_vec) functions. **But note that when using these asynchronous functions, you can not use backlash or hysteresis compensation.**

## Configuration

The maximum motor speed and acceleration can be configured with the [`set_max_speed(index, speed)`](doc/stepper_board.md#stepper_board.StepperBoard.set_max_speed) and [`set_max_accel(index, accel)`](doc/stepper_board.md#stepper_board.StepperBoard.set_max_accel) methods. The maximum speed is specified in microsteps per second, and the acceleration in microsteps per second squared. The current maximum speed and acceleration can be queried with the [`max_speed(index)`](doc/stepper_board.md#stepper_board.StepperBoard.max_speed) and [`max_accel(index)`](doc/stepper_board.md#stepper_board.StepperBoard.max_accel) or [`max_speed_vec()`](doc/stepper_board.md#stepper_board.StepperBoard.max_speed_vec) and [`max_accel_vec()`](doc/stepper_board.md#stepper_board.StepperBoard.max_accel_vec) methods.

The speed is specified in microsteps per second, and the acceleration in microsteps per second squared.

The maximum speed and acceleration that a motor can be driven at before it starts losing steps depends on many factors. These include the motor itself, the load and load inertia, the supply voltage, the maximum drive current, and a few more.

To find the maximum speed, set the motor to a safe low acceleration and increase the speed until the motor starts losing steps. Then set the speed to a slightly lower value to allow for some margin. To find the maximum acceleration set the motor to the highest speed that it can reliably reach and increase the acceleration until the motor starts losing steps. Then, again, set the acceleration to a slightly lower value to allow for some margin.

## Backlash and Hysteresis Compensation

The driver board can be run in backlash or hysteresis compensation mode, which can be enabled with the [`set_compensation(mode)`](doc/stepper_board.md#stepper_board.StepperBoard.set_compensation) method, where mode is either `"backlash"`, `"hysteresis"` or `"none"`. For backlash compensation, backlash needs to be specified for each stepper with the [`set_backlash(index, steps)`](doc/stepper_board.md#stepper_board.StepperBoard.set_backlash) method, where steps is the backlash in microsteps. For hysteresis compensation, the hysteresis compensation needs to be specified for each stepper with the [`set_hysteresis(index, steps)`](doc/stepper_board.md#stepper_board.StepperBoard.set_hysteresis) method, where steps is the step offset in microsteps that the final position should be approached from. The compensation can only be set for all steppers at the same time. The current compensation mode, backlash, and hysteresis settings can be queried with the [`compensation()`](doc/stepper_board.md#stepper_board.StepperBoard.compensation), [`backlash(index)`](doc/stepper_board.md#stepper_board.StepperBoard.backlash,) and [`hysteresis(index)`](doc/stepper_board.md#stepper_board.StepperBoard.hysteresis) methods.

## Other Functions

The current position and target can be queried with the [`position(index)`](doc/stepper_board.md#stepper_board.StepperBoard.position) and [`target(index)`](doc/stepper_board.md#stepper_board.StepperBoard.target) methods or their vector equivalents [`position_vec()`](doc/stepper_board.md#stepper_board.StepperBoard.position_vec) and [`target_vec()`](doc/stepper_board.md#stepper_board.StepperBoard.target_vec).

The stored position of a single stepper, or all steppers at once, can be reset to zero with the [`set_home(index)`](doc/stepper_board.md#stepper_board.StepperBoard.set_home) and [`set_home_vec()`](doc/stepper_board.md#stepper_board.StepperBoard.set_home_vec) methods.

The board and axes can be named with [`set_board_name(name)`](doc/stepper_board.md#stepper_board.StepperBoard.set_board_name) and [`set_axis_name(index, name)`](doc/stepper_board.md#stepper_board.StepperBoard.set_axis_name) methods. The names can be queried with [`board_name()`](doc/stepper_board.md#stepper_board.StepperBoard.board_name) and [`axis_name(index)`](doc/stepper_board.md#stepper_board.StepperBoard.axis_name) methods.

Finally, the configuration can be reset to the firmware defaults with the [`reset_config()`](doc/stepper_board.md#stepper_board.StepperBoard.reset_config) method and the firmware version can be queried with the [`firmware_version()`](doc/stepper_board.md#stepper_board.StepperBoard.firmware_version) method.

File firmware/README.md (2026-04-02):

# Firmware for Stepper Driver Board

The stepper driver board precisely generates the pulses and other electrical signals required to address the stepper drivers / stepsticks. It also handles backlash and hysteresis compensation.

## Flashing Pre-Compiled Firmware

1. Install [`esptool`](https://pypi.org/project/esptool/) for example using pip:

    ```shell
    pip install esptool
    ```

2. Erase the flash memory of the controller board using:

    ```shell
    esptool --chip esp32s3 erase_flash
    ```

    If you have multiple serial devices connected, you may also need to specify the port using `--port COM[X]` on Windows or `--port /dev/ttyUSB[X]` on Linux.

3. Flash the image using:

    ```shell
    esptool --chip esp32s3 write_flash 0x0 firmware.bin
    ```

    The same note about the port applies here as well.

## Building from Source

0. _Use Linux, don't try to do this on Windows. And if you plan on doing actual development work rather than building once, consider working on the WSL file system instead of Windows. This significantly reduce compile times._
1. Install the Rust toolchain with [rustup](https://rustup.rs/) or your system's package manager.
2. Install [espup](https://github.com/esp-rs/espup) as described in the guide. _Note: Since [`rust-toolchain.toml`](rust-toolchain.toml) overwrites the toolchain to `esp` (which is not installed at this point) you need to run `cargo install espup --locked` in a different directory or temperarily remove the `rust-toolchain.toml` file to be able to run cargo._
3. Install [espflash](https://crates.io/crates/espflash) and [ldproxy](https://crates.io/crates/ldproxy) with:

    ```shell
    cargo install espflash ldproxy
    ```

4. Build the firmware with:

    ```shell
    cargo build
    ```

    ... or flash and run it with:

    ```shell
    cargo run
    ```

    If you use WSL, you will need to forward the serial port to WSL with [usbipd](https://learn.microsoft.com/en-us/windows/wsl/connect-usb).

5. Optionally, make a flashable image by running:

    ```shell
    espflash save-image --chip esp32s3 target/xtensa-esp32s3-espidf/debug/stepper-driver-board firmware.bin --merge
    ```

    This will create a [`firmware.bin`](firmware.bin) file than can be flashed with [esptool](https://pypi.org/project/esptool/) later.
    Note that the paths assume that you are running this from the `firmware` directory.

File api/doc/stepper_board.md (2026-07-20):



# stepper\_board

RPC stub class for the stepper driver board.

#### LARGE\_FLOAT

Large "effectively infinite" float because json doesn't support inf

#### Number

A number can be an int or a float

## StepperBoard Objects

```python
class StepperBoard(rpc.RpcProxy)
```

#### move\_to

```python
def move_to(index: int, target: int, speed: Number = LARGE_FLOAT) -> None
```

Move a stepper with given index to a target position at a given speed, blocking until the move is complete

**Arguments**:

- `index` _int_ - The index of the stepper to move
- `target` _int_ - The target position to move to
- `speed` _Number, optional_ - The speed to move at. Defaults to LARGE_FLOAT.

#### wait

```python
def wait(index: int) -> None
```

Wait for a stepper with given index to finish moving

**Arguments**:

- `index` _int_ - The index of the stepper to wait for

#### set\_target

```python
def set_target(index: int, target: int, speed: Number = LARGE_FLOAT) -> None
```

Set the target position of a stepper with given index, non-blocking version of move_to

**Arguments**:

- `index` _int_ - The index of the stepper to set the target of
- `target` _int_ - The target position to set
- `speed` _Number, optional_ - The speed to move at. Defaults to LARGE_FLOAT.

#### stop

```python
def stop(index: int) -> None
```

Stop a stepper with given index

**Arguments**:

- `index` _int_ - The index of the stepper to stop

#### set\_home

```python
def set_home(index: int) -> None
```

Set the current position of a stepper with given index as the home (zero) position

**Arguments**:

- `index` _int_ - The index of the stepper to set the home of

#### position

```python
def position(index: int) -> int
```

Get the current position of a stepper with given index

**Arguments**:

- `index` _int_ - The index of the stepper to get the position of

**Returns**:

- `int` - The current position of the stepper

#### target

```python
def target(index: int) -> int
```

Get the target position of a stepper with given index

**Arguments**:

- `index` _int_ - The index of the stepper to get the target of

**Returns**:

- `int` - The target position of the stepper

#### steps\_remaining

```python
def steps_remaining(index: int) -> int
```

Get the number of steps remaining for a stepper with given index to reach its target

**Arguments**:

- `index` _int_ - The index of the stepper to get the steps remaining of

**Returns**:

- `int` - The number of steps remaining for the stepper to reach its target

#### time\_remaining

```python
def time_remaining(index: int) -> float
```

Get the approximate time remaining for a stepper with given index to reach its target

**Arguments**:

- `index` _int_ - The index of the stepper to get the time remaining of

**Returns**:

- `float` - The approximate time remaining for the stepper to reach its target, the time will sometimes be slightly overestimated

#### max\_speed

```python
def max_speed(index: int) -> float
```

Get the maximum speed of a stepper with given index

**Arguments**:

- `index` _int_ - The index of the stepper to get the maximum speed of

**Returns**:

- `float` - The maximum speed of the stepper

#### set\_max\_speed

```python
def set_max_speed(index: int, speed: Number) -> None
```

Set the maximum speed of a stepper with given index

**Arguments**:

- `index` _int_ - The index of the stepper to set the maximum speed of
- `speed` _Number_ - The maximum speed to set

#### max\_accel

```python
def max_accel(index: int) -> float
```

Get the maximum acceleration of a stepper with given index

**Arguments**:

- `index` _int_ - The index of the stepper to get the maximum acceleration of

**Returns**:

- `float` - The maximum acceleration of the stepper

#### set\_max\_accel

```python
def set_max_accel(index: int, speed: Number) -> None
```

Set the maximum acceleration of a stepper with given index

**Arguments**:

- `index` _int_ - The index of the stepper to set the maximum acceleration of
- `speed` _Number_ - The maximum acceleration to set

#### move\_to\_vec

```python
def move_to_vec(targets: list[int],
                mode: str,
                speed: Number = LARGE_FLOAT) -> None
```

Move all steppers to the given target positions at the given speed, blocking until all steppers have reached their targets

**Arguments**:

- `targets` _list[int]_ - The target positions to move to. If the list is shorter than the number of steppers the list will be padded with zeros
- `mode` _str_ - Joint movement mode:
  - "individual_max": Each stepper moves to its target at its maximum speed, the steppers generally finish at different times
  - "joint_max": The steppers speeds are adjusted so that the path is linearly interpolated and they all finish at the same time. The speed is determined by the max speed of the stepper that takes the longest time to reach its target.
  - "joint_euclid": The steppers speeds are adjusted so that the path is linearly interpolated and they all finish at the same time. The euclidean norm of the speeds must be specified.
  - "joint_cheby": The steppers speeds are adjusted so that the path is linearly interpolated and they all finish at the same time. The chebyshev norm (max of the absolute values) of the speeds must be specified.
- `speed` _Number, optional_ - Speed for "joint_euclid" and "joint_cheby" modes. Defaults to LARGE_FLOAT.

#### wait\_vec

```python
def wait_vec() -> None
```

Wait for all steppers to finish moving

#### set\_target\_vec

```python
def set_target_vec(targets: list[int],
                   mode: str,
                   speed: Number = LARGE_FLOAT) -> None
```

Set the target positions of all steppers, non-blocking version of move_to_vec

**Arguments**:

- `targets` _list[int]_ - The target positions to set. If the list is shorter than the number of steppers the list will be padded with zeros
- `mode` _str_ - Joint movement mode:
  - "individual_max": Each stepper moves to its target at its maximum speed, the steppers generally finish at different times
  - "joint_max": The steppers speeds are adjusted so that the path is linearly interpolated and they all finish at the same time. The speed is determined by the max speed of the stepper that takes the longest time to reach its target.
  - "joint_euclid": The steppers speeds are adjusted so that the path is linearly interpolated and they all finish at the same time. The euclidean norm of the speeds must be specified.
  - "joint_cheby": The steppers speeds are adjusted so that the path is linearly interpolated and they all finish at the same time. The chebyshev norm (max of the absolute values) of the speeds must be specified.
- `speed` _Number, optional_ - Speed for "joint_euclid" and "joint_cheby" modes. Defaults to LARGE_FLOAT.

#### stop\_vec

```python
def stop_vec() -> None
```

Stop all steppers

#### set\_home\_vec

```python
def set_home_vec() -> None
```

Set the current positions of all steppers as the home (zero) positions

#### position\_vec

```python
def position_vec() -> list[int]
```

Get the current positions of all steppers

**Returns**:

- `list[int]` - The current positions of all steppers

#### target\_vec

```python
def target_vec() -> list[int]
```

Get the target positions of all steppers

**Returns**:

- `list[int]` - The target positions of all steppers

#### steps\_remaining\_vec

```python
def steps_remaining_vec() -> list[int]
```

Get the number of steps remaining for all steppers to reach their targets

**Returns**:

- `list[int]` - The number of steps remaining for all steppers to reach their targets

#### time\_remaining\_vec

```python
def time_remaining_vec() -> float
```

Get the approximate time remaining until all steppers reach their targets

**Returns**:

- `float` - The approximate time remaining until all steppers reach their targets, the time will sometimes be slightly overestimated

#### max\_speed\_vec

```python
def max_speed_vec() -> list[float]
```

Get the maximum speeds of all steppers

**Returns**:

- `list[float]` - The maximum speeds of all steppers

#### max\_accel\_vec

```python
def max_accel_vec() -> list[float]
```

Get the maximum accelerations of all steppers

**Returns**:

- `list[float]` - The maximum accelerations of all steppers

#### board\_name

```python
def board_name() -> str
```

Get the name of the stepper board

**Returns**:

- `str` - The name of the stepper board

#### set\_board\_name

```python
def set_board_name(name: str) -> None
```

Set the name of the stepper board

**Arguments**:

- `name` _str_ - The name to set for the stepper board

#### axis\_name

```python
def axis_name(index: int) -> str
```

Get the name of a stepper with given index

**Arguments**:

- `index` _int_ - The index of the stepper to get the name of

**Returns**:

- `str` - The name of the stepper

#### set\_axis\_name

```python
def set_axis_name(index: int, name: str) -> None
```

Set the name of a stepper with given index

**Arguments**:

- `index` _int_ - The index of the stepper to set the name of
- `name` _str_ - The name to set for the stepper

#### enabled

```python
def enabled() -> bool
```

Query whether the physical stepper drivers (stepsticks) are enabled

If the drivers are disabled they will no longer drive any (holding) current. The stepper board will refuse to move the stepper until the drivers are enabled again.

**Returns**:

- `bool` - True if the drivers are enabled, False if they are disabled

#### set\_enabled

```python
def set_enabled(enable: bool) -> None
```

Enable or disable the physical stepper drivers (stepsticks)

If the drivers are disabled they will no longer drive any (holding) current. The stepper board will refuse to move the stepper until the drivers are enabled again.

**Arguments**:

- `enable` _bool_ - True to enable the drivers, False to disable them

#### microsteps

```python
def microsteps() -> int
```

Get the number of microsteps per full step (step pulses required per full step) that the stepper drivers are currently configured for

**Returns**:

- `int` - The number of microsteps per full step

#### set\_microsteps

```python
def set_microsteps(microsteps: int) -> None
```

Set the number of microsteps per full step (step pulses required per full step) that the stepper drivers should be configured for

**Arguments**:

- `microsteps` _int_ - The number of microsteps per full step. Must be one of [2, 4, 8, 16]

#### timeout

```python
def timeout() -> int
```

Get the auto-shutdown timeout in seconds, if the board receives no commands for this duration it will disable the stepper drivers

**Returns**:

- `int` - The auto-shutdown timeout in seconds, 0 means no timeout

#### set\_timeout

```python
def set_timeout(timeout: int) -> None
```

Set the auto-shutdown timeout in seconds, if the board receives no commands for this duration it will disable the stepper drivers

**Arguments**:

- `timeout` _int_ - The auto-shutdown timeout in seconds, 0 means no timeout

#### compensation

```python
def compensation() -> str
```

Get the current compensation type

The available compensation types are:
- "none": No compensation is applied
- "backlash": Backlash compensation is applied. When the stepper changes direction the stepper will add an additional number of steps to the target position according to the specified backlash value
- "hysteresis": Hysteresis compensation is applied. The driver will always approach the target position from a given offset determined by the specified hysteresis value

**Returns**:

- `str` - The current compensation type

#### set\_compensation

```python
def set_compensation(compensation_type: str) -> None
```

Set the compensation type

The available compensation types are:
- "none": No compensation is applied
- "backlash": Backlash compensation is applied. When the stepper changes direction the stepper will add an additional number of steps to the target position according to the specified backlash value
- "hysteresis": Hysteresis compensation is applied. The driver will always approach the target position from a given offset determined by the specified hysteresis value

**Arguments**:

- `compensation_type` _str_ - The compensation type to set

#### backlash

```python
def backlash(index: int) -> int
```

Get the backlash compensation value for a stepper with given index

**Arguments**:

- `index` _int_ - The index of the stepper to get the backlash compensation value of

**Returns**:

- `int` - The backlash compensation value

#### set\_backlash

```python
def set_backlash(index: int, value: int) -> None
```

Set the backlash compensation value for a stepper with given index

**Arguments**:

- `index` _int_ - The index of the stepper to set the backlash compensation value of
- `value` _int_ - The backlash compensation value to set

#### hysteresis

```python
def hysteresis(index: int) -> int
```

Get the hysteresis compensation value for a stepper with given index

**Arguments**:

- `index` _int_ - The index of the stepper to get the hysteresis compensation value of

**Returns**:

- `int` - The hysteresis compensation value

#### set\_hysteresis

```python
def set_hysteresis(index: int, value: int) -> None
```

Set the hysteresis compensation value for a stepper with given index

**Arguments**:

- `index` _int_ - The index of the stepper to set the hysteresis compensation value of
- `value` _int_ - The hysteresis compensation value to set

#### reset\_config

```python
def reset_config() -> None
```

Reset the configuration of the stepper board to default values

#### firmware\_version

```python
def firmware_version() -> str
```

Get the firmware version of the stepper board

**Returns**:

- `str` - The firmware version of the stepper board

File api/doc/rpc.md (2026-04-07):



# rpc

Minimalist RPC implementation over a bidirectional line stream like a serial port or TCP socket

## BidirectionalLineStream Objects

```python
class BidirectionalLineStream(ABC)
```

Abstract base class for a bidirectional line stream. Implementations should be able to read and write lines.

#### read\_line

```python
@abstractmethod
def read_line() -> str
```

Read a line from the stream and return it as a string

**Returns**:

- `str` - The line read from the stream

#### write\_line

```python
@abstractmethod
def write_line(line: str)
```

Write a line to the stream

#### close

```python
@abstractmethod
def close()
```

Close the underlying transport

## SerialBLS Objects

```python
class SerialBLS(BidirectionalLineStream)
```

A bidirectional line stream with a serial port as the backend

#### \_\_init\_\_

```python
def __init__(serial_port: Serial, print_non_json=False)
```

Create a new SerialBLS instance from a serial port

**Arguments**:

- `serial_port` _Serial_ - The serial port to use
- `print_non_json` _bool, optional_ - Print non-json (non protocol) lines to stdout. Defaults to False.

#### connect

```python
@staticmethod
def connect(port: str, baudrate: int, print_non_json=False) -> Self
```

Connect to a serial port and return a SerialBLS instance

**Arguments**:

- `port` _str_ - The port to connect to
- `baudrate` _int_ - The baudrate to use
- `print_non_json` _bool, optional_ - Print non-json (non protocol) lines to stdout. Defaults to False.

**Returns**:

- `SerialBLS` - The SerialBLS instance

## SocketBLS Objects

```python
class SocketBLS(BidirectionalLineStream)
```

A bidirectional line stream with a socket as the backend

#### \_\_init\_\_

```python
def __init__(sock: socket.socket, print_non_json: bool = False)
```

Create a new SocketBLS instance from a socket

**Arguments**:

- `sock` _socket.socket_ - The socket to use
- `print_non_json` _bool, optional_ - Print non-json (non protocol) lines to stdout. Defaults to False.

#### connect

```python
@staticmethod
def connect(host: str, port: int, print_non_json: bool = False) -> Self
```

Connect to a socket and return a SocketBLS instance

**Arguments**:

- `host` _str_ - The host to connect to
- `port` _int_ - The port to connect to
- `print_non_json` _bool, optional_ - Print non-json (non protocol) lines to stdout. Defaults to False.

**Returns**:

- `SocketBLS` - The SocketBLS instance

## RpcClient Objects

```python
class RpcClient()
```

A client class over which to call procedures on a remote server

#### \_\_init\_\_

```python
def __init__(bls: BidirectionalLineStream)
```

Create a new RpcClient instance

**Arguments**:

- `bls` _BidirectionalLineStream_ - The bidirectional line stream to use

#### read\_response

```python
def read_response(id: int) -> dict
```

Read a response from the server (or from the internal response buffer) with the specified id

All other responses read while awaiting the specified id are stored internally

**Arguments**:

- `id` _int_ - The id of the response to read

#### call

```python
def call(method: str, *args) -> Any
```

Call a remote procedure with the specified method name and arguments

**Arguments**:

- `method` _str_ - The name of the method to call
- `*args` - The arguments to pass to the method

**Returns**:

- `Any` - The result of the remote procedure call

**Raises**:

- `ValueError` - If the remote procedure call server returns an error or the procedure errors

#### register

```python
def register(method: Callable) -> Callable
```

Wrap a stub method so that it is called remotely via this instance

Since this is a method that takes a function and returns a function, it can be used as a decorator.
The stub must have type hints for all arguments as true types and not strings.
The types will be checked when calling and the wrapped method will raise if the types are incorrect before attempting to call the remote procedure.
Generic aliases eg list[int] will only check the base type (list) and not the inner type (int).

**Arguments**:

- `method` _Callable_ - The method to wrap

**Returns**:

- `Callable` - The wrapped method

## RpcProxy Objects

```python
class RpcProxy()
```

This class can be inherited from by a class made up of stub methods to wrap them for remote procedure calls

On initialization all methods that do not start with an underscore will be replaced by a wrapped version that calls the respective
method on the remote that is passed in the constructor.

#### \_\_init\_\_

```python
def __init__(client: RpcClient)
```

Create a new RpcProxy instance

**Arguments**:

- `client` _RpcClient_ - The client to use for remote procedure calls

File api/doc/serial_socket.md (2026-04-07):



# serial\_socket

Expose a serial device as a TCP socket.

## SerialSocketBridge Objects

```python
class SerialSocketBridge()
```

Bridge raw traffic between a serial port and TCP socket.

#### \_\_init\_\_

```python
def __init__(serial_port: str, baudrate: int, host: str, port: int)
```

Create a new SerialSocketBridge instance.

**Arguments**:

- `serial_port` _str_ - Serial device path, e.g. COM3 or /dev/ttyUSB0
- `baudrate` _int_ - Serial baudrate
- `host` _str_ - TCP host/interface to bind
- `port` _int_ - TCP port to bind

#### serve\_forever

```python
def serve_forever() -> NoReturn
```

Run the bridge server until interrupted.

#### main

```python
def main(argv: list[str] | None = None)
```

Entry point for the serial socket bridge CLI.

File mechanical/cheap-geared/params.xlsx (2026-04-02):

Name | Value | Unit | Comment
thumbscrew_dia | 15.8 | mm
helix_length | 3.5 | mm
helix_width | 2 | mm
helix_fillet | 0.3 | mm
helix_teeth | 8 | ul
helix_inner_dia | 19 | mm
helix_outer_dia | 23 | mm
elephant_prevention_radius | 0.3 | mm
gear_center_distance | 25 | mm
stepper_screw_dist | 35 | mm
stepper_axis_offset | 8 | mm
stepper_axis_clearance | 10 | mm
mount_screw_ortho_dist | 31 | mm
stepper_dia | 28 | mm
sheet_thick | 2.5 | mm
helix_winding_factor | 1.2 | ul

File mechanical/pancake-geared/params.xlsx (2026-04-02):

Name | Value | Unit | Comment
thumbscrew_dia | 15.8 | mm
helix_length | 3.5 | mm
helix_width | 2 | mm
helix_fillet | 0.3 | mm
helix_teeth | 8 | ul
helix_inner_dia | 19 | mm
helix_outer_dia | 23 | mm
elephant_prevention_radius | 0.3 | mm
gear_center_distance | 25 | mm
stepper_screw_dist | 43.85 | mm
stepper_axis_offset | 0 | mm
stepper_axis_clearance | 16.5 | mm
mount_screw_ortho_dist | 31 | mm
stepper_dia | 36.3 | mm
sheet_thick | 2.5 | mm
helix_winding_factor | 1.2 | ul

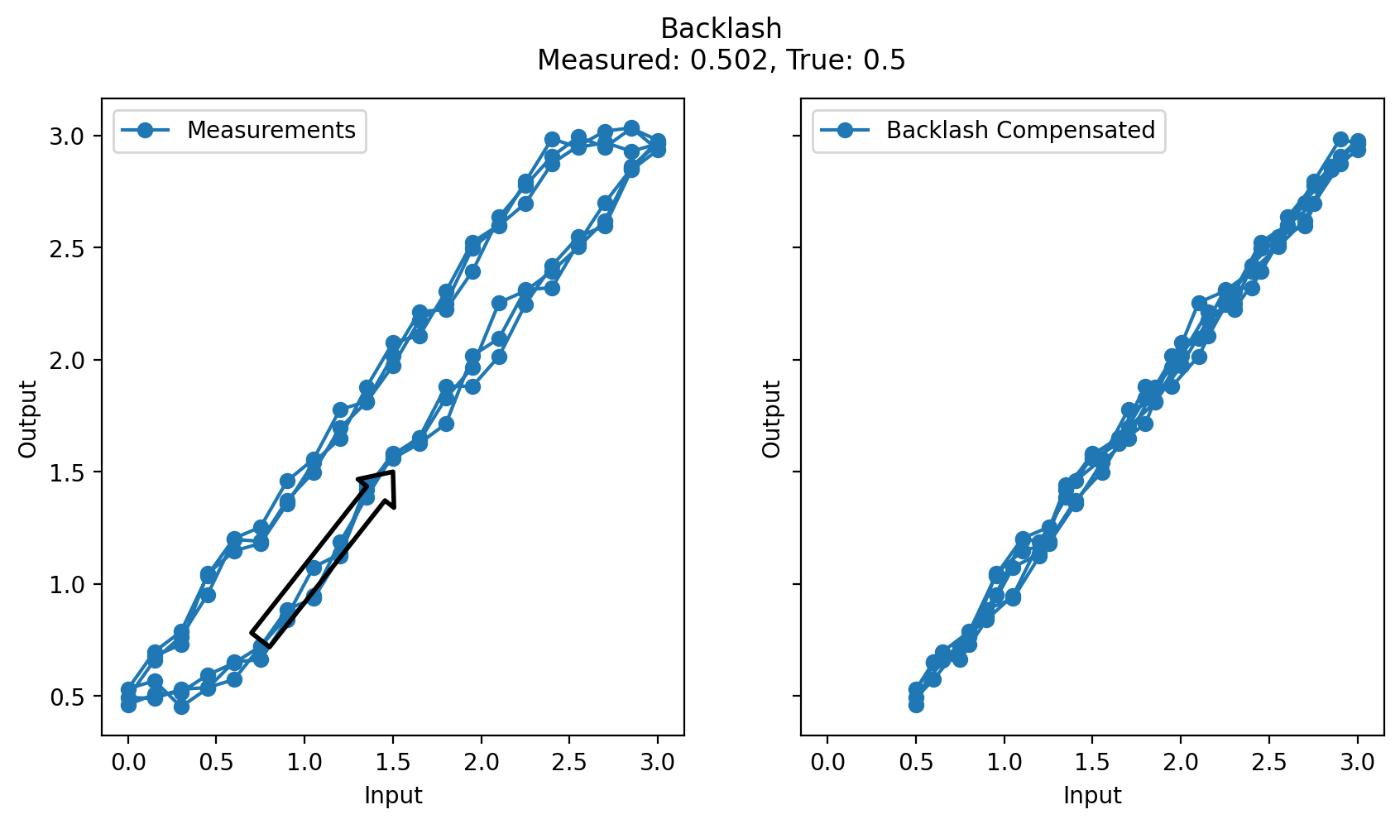
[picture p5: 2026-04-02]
images/plots/backlash.png

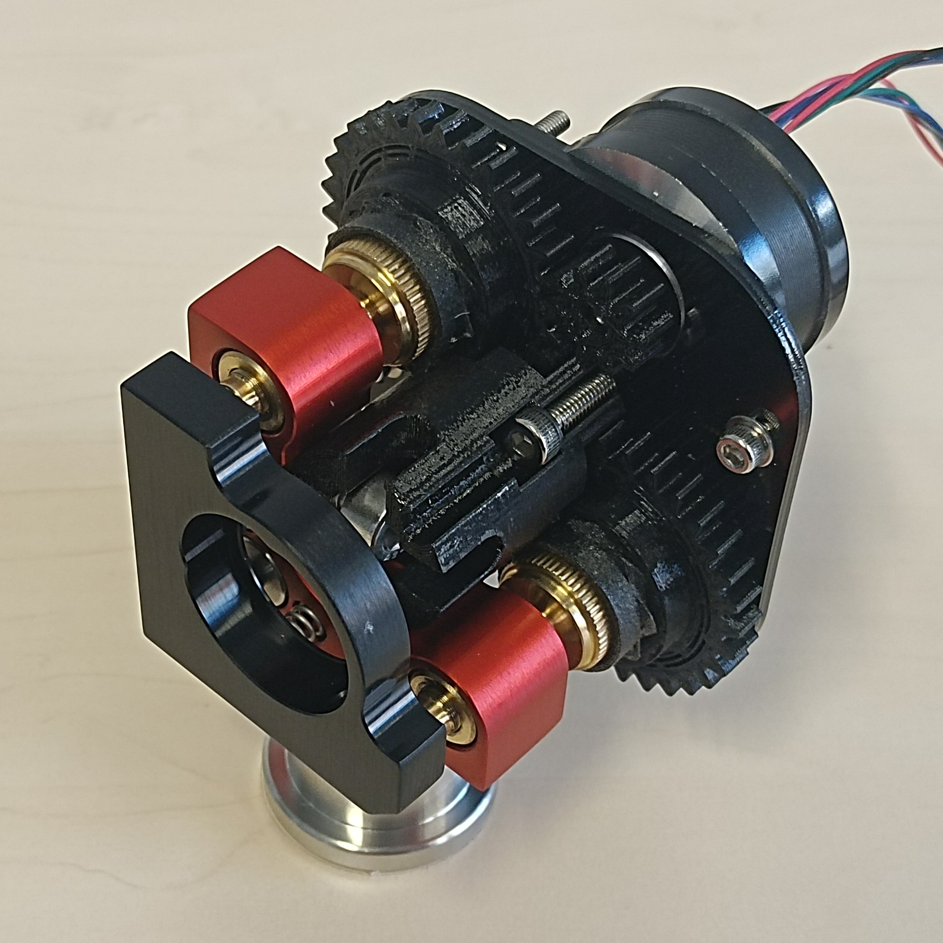
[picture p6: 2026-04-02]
images/models/pancake-geared-front.jpg

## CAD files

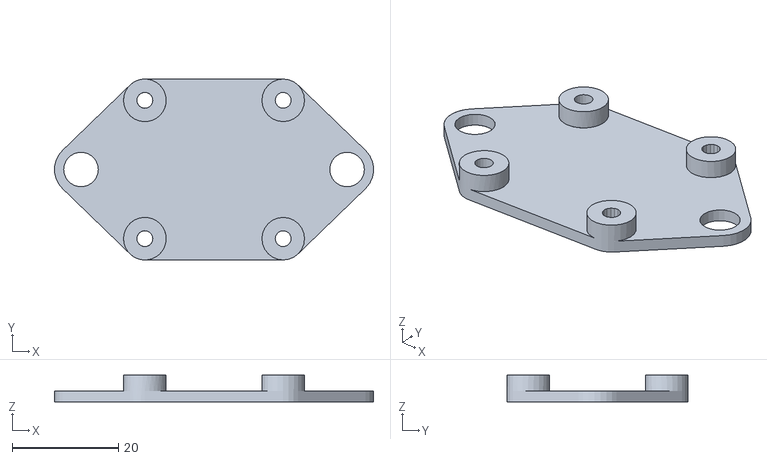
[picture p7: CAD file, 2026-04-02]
mechanical/adapter-board/adapter-board-mount.stl
59.9 x 34.0 x 5.00

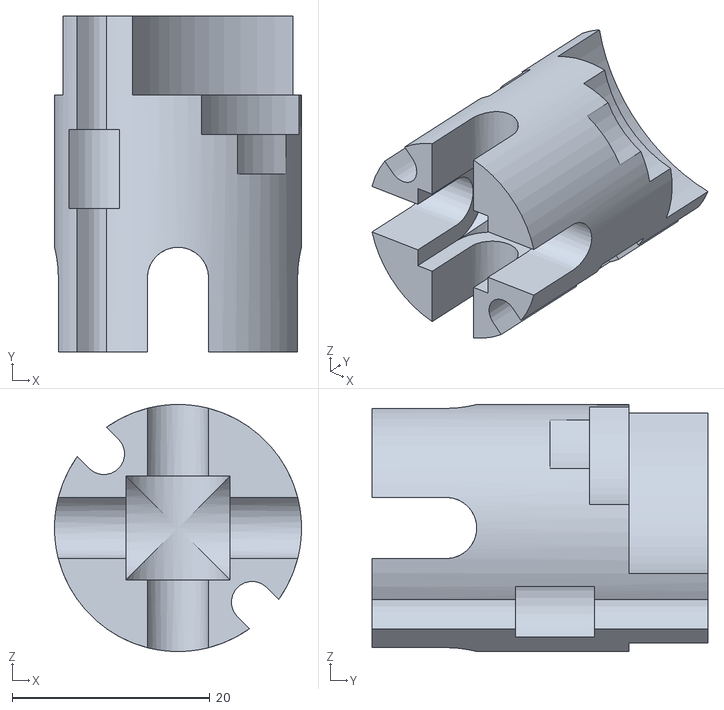
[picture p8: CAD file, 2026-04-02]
mechanical/cheap-direct/mount-stem.stl
25.0 x 34.0 x 25.0

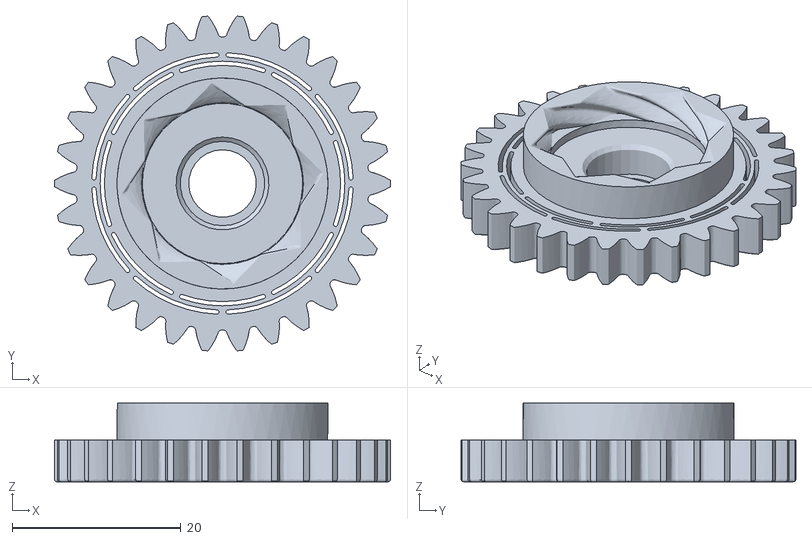
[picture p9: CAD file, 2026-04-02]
mechanical/cheap-geared/gear.stl
39.8 x 39.7 x 9.35

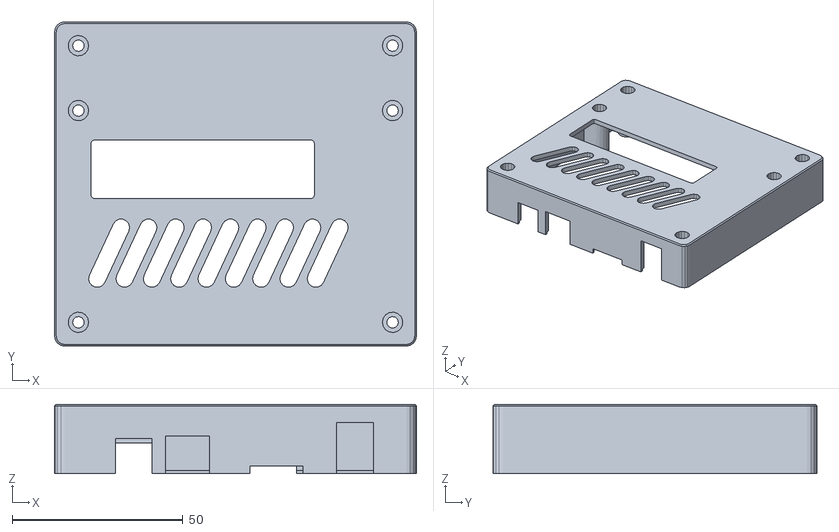
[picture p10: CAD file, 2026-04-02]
mechanical/driver-board-case/driver-board-case-upper.stl
106.0 x 95.0 x 20.3

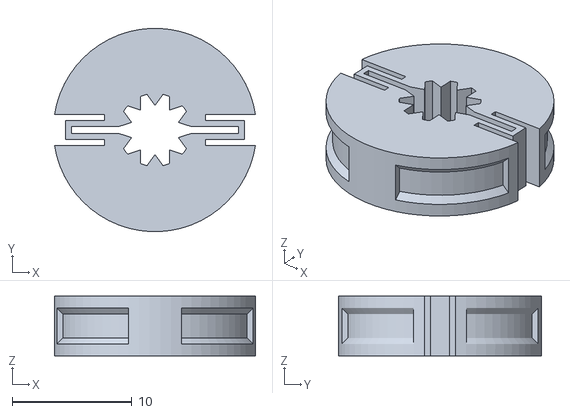
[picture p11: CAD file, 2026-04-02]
mechanical/pancake-direct-v2/gear-grip.stl
16.8 x 17.0 x 5.00

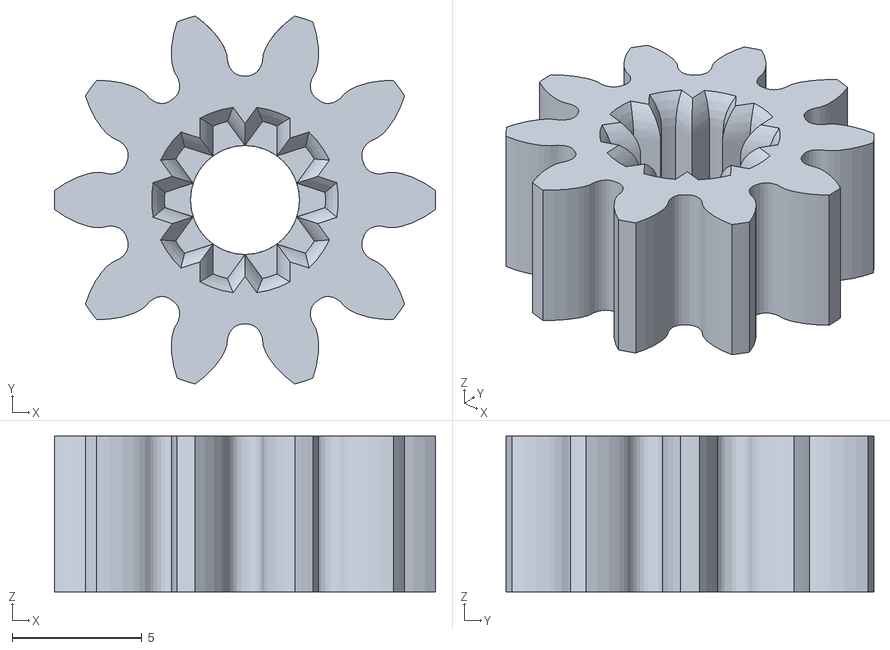
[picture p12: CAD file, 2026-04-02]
mechanical/pancake-geared/pinion.stl
14.7 x 14.2 x 6.00

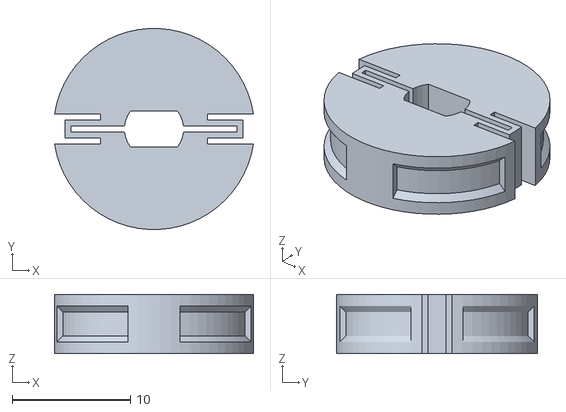
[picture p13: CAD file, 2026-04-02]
mechanical/cheap-direct/shaft-grip.stl
16.8 x 17.0 x 5.00

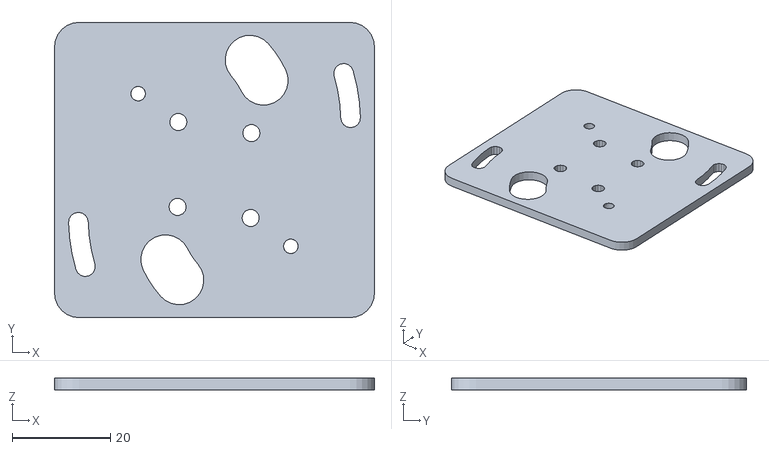
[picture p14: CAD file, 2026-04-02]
mechanical/cheap-geared/mount-plate.stl
65.0 x 60.0 x 2.50

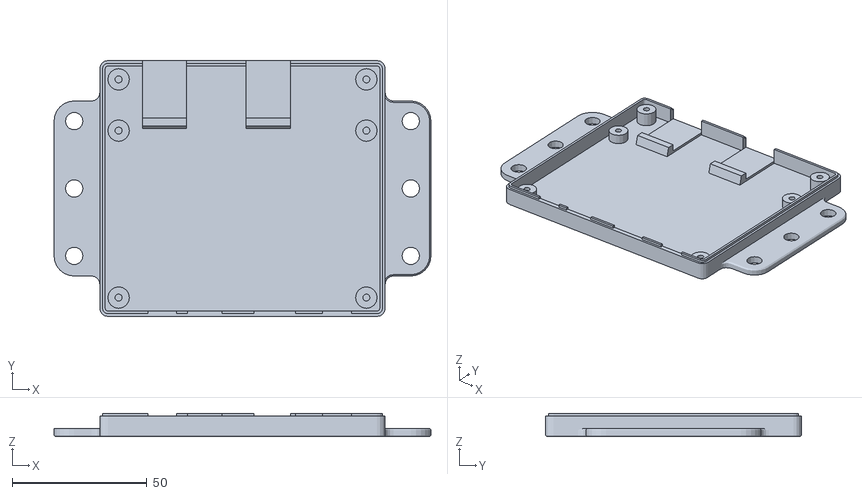
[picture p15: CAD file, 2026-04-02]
mechanical/driver-board-case/driver-board-case-lower.stl
140.0 x 95.0 x 8.65

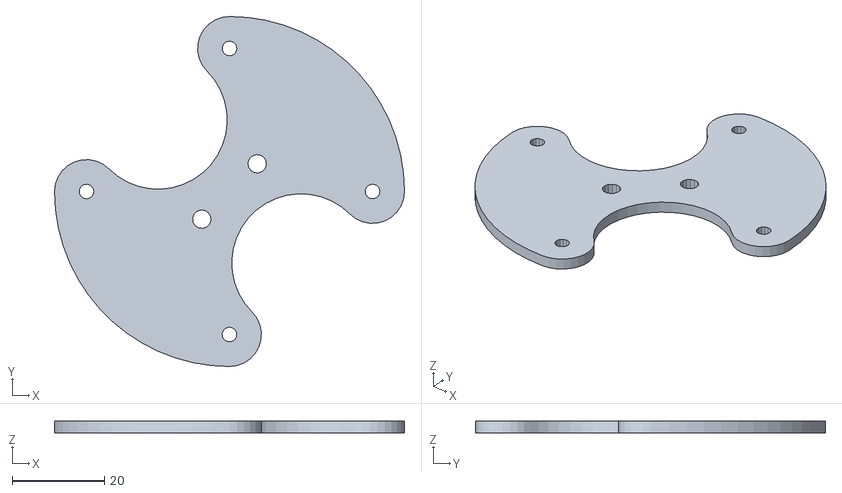
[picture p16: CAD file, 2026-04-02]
mechanical/pancake-direct-v2/mount-plate.stl
75.9 x 75.9 x 2.50

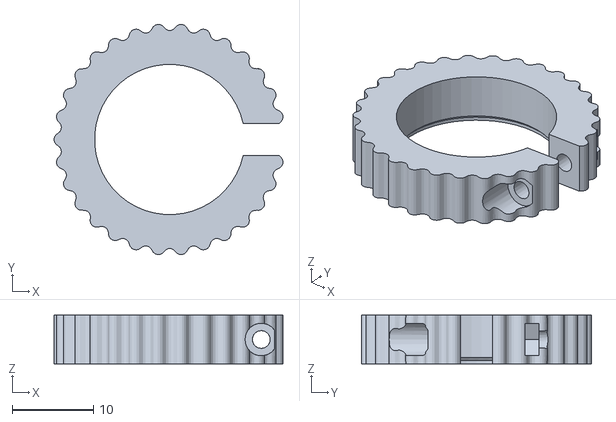
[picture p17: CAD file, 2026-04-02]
mechanical/pancake-direct/fastener.stl
28.2 x 28.3 x 6.00

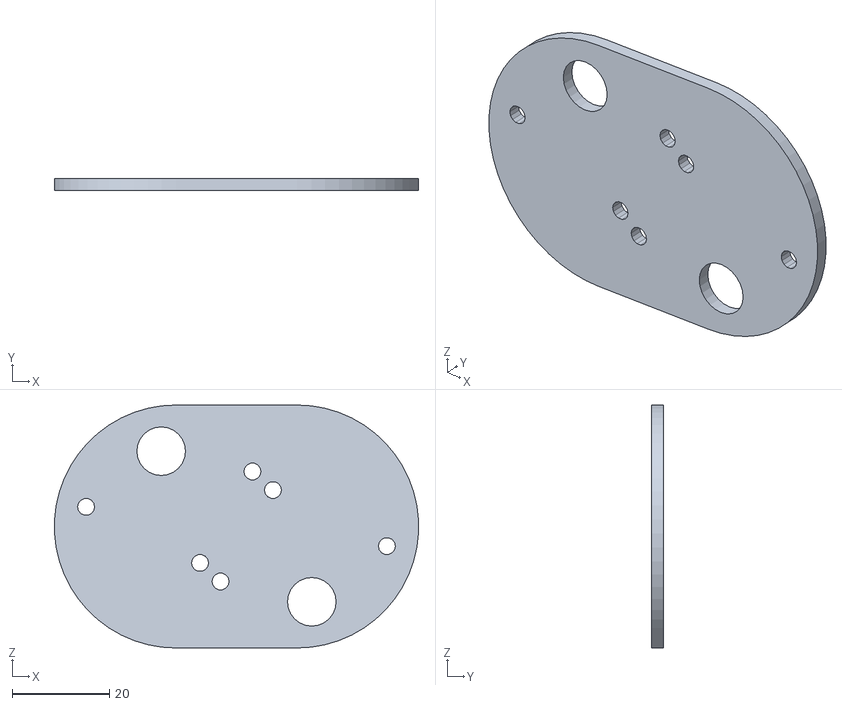
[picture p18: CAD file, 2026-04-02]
mechanical/cheap-direct/mount-plate.stl
74.9 x 2.50 x 50.0

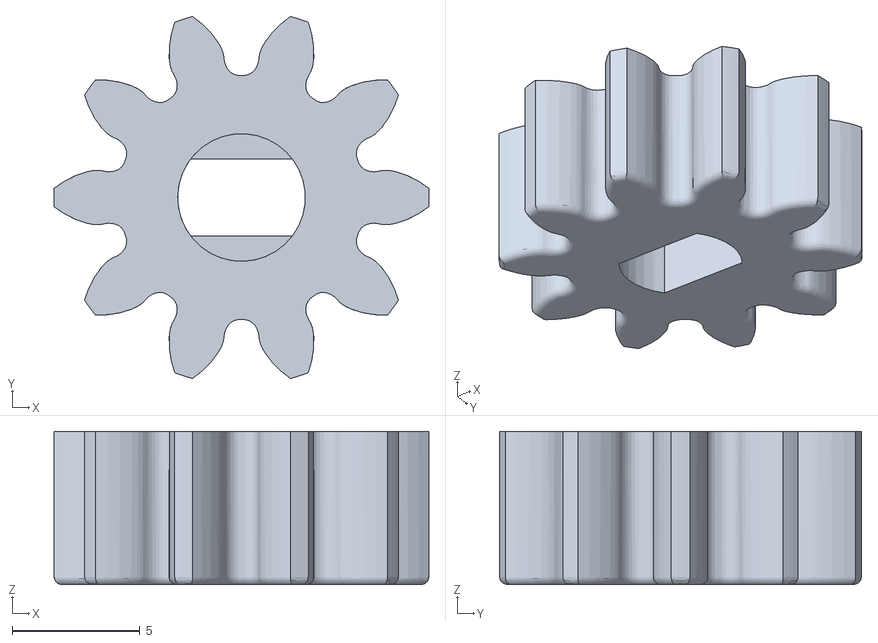
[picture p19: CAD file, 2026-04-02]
mechanical/cheap-geared/pinion.stl
14.7 x 14.2 x 6.00

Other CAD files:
mechanical/adapter-board/adapter-board-mount.ipt
mechanical/cheap-direct/fastener.ipt
mechanical/cheap-direct/mount-plate.dxf
mechanical/cheap-direct/mount-plate.ipt
mechanical/cheap-direct/mount-stem.ipt
mechanical/cheap-direct/screw-grip.ipt
mechanical/cheap-direct/screw-grip.stl
mechanical/cheap-direct/shaft-grip.ipt
mechanical/cheap-geared/cheap-geared.iam
mechanical/cheap-geared/mount-plate.dxf
mechanical/cheap-geared/mount-plate.ipt
mechanical/cheap-geared/mount-stem.ipt
mechanical/cheap-geared/pinion.ipt
mechanical/cheap-geared/screw-grip.ipt
mechanical/cheap-geared/screw-grip.stl
mechanical/cheap-geared/washer.dxf
mechanical/cheap-geared/washer.ipt
mechanical/cheap-geared/washer.stl
mechanical/driver-board-case/driver-board-case.ipt
mechanical/pancake-direct-v2/fastener.ipt
mechanical/pancake-direct-v2/gear-grip.ipt
mechanical/pancake-direct-v2/gear-grip.newVer.ipt
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

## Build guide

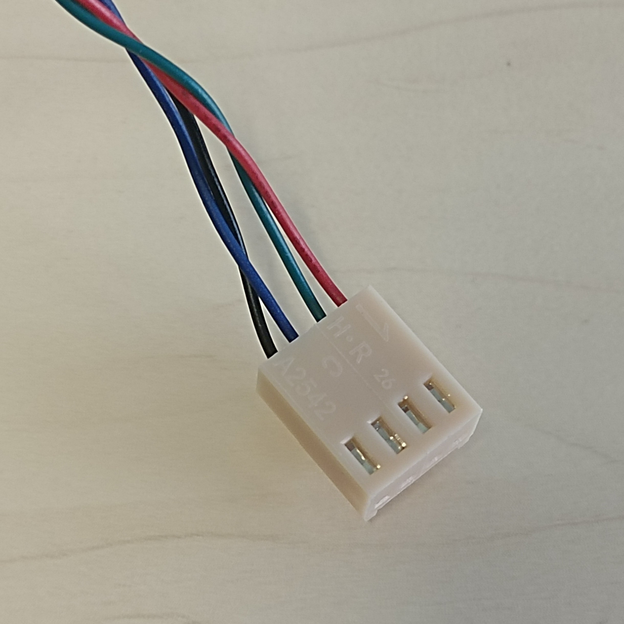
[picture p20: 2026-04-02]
images/instructions/step_01.jpg

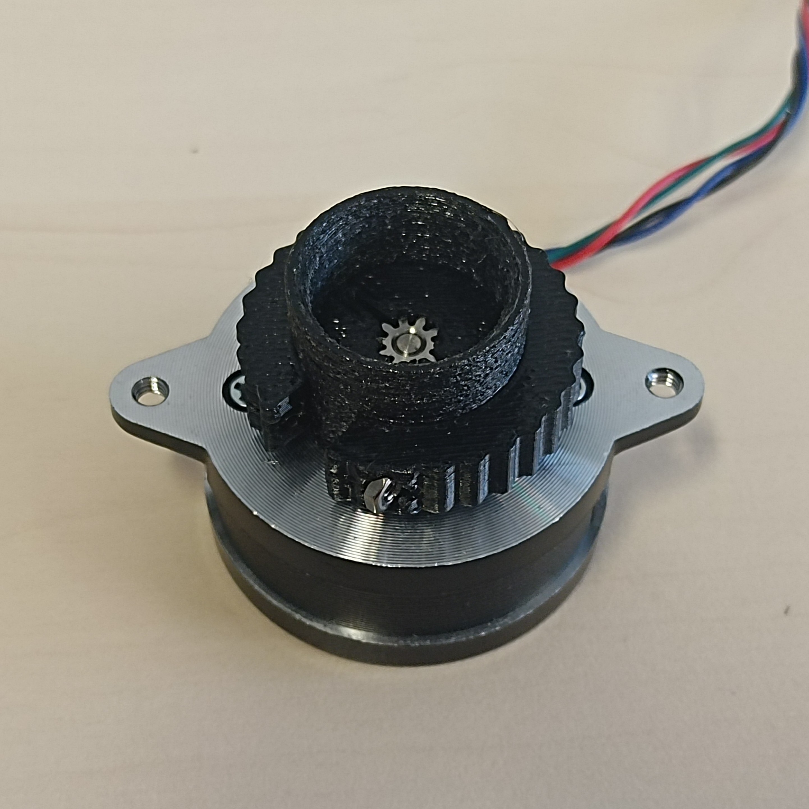
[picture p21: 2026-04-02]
images/instructions/step_05.jpg

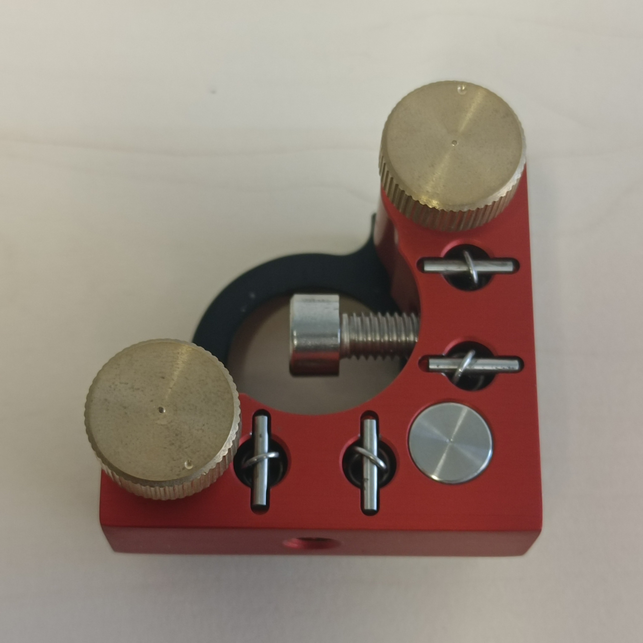
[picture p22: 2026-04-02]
images/instructions/step_12.jpg

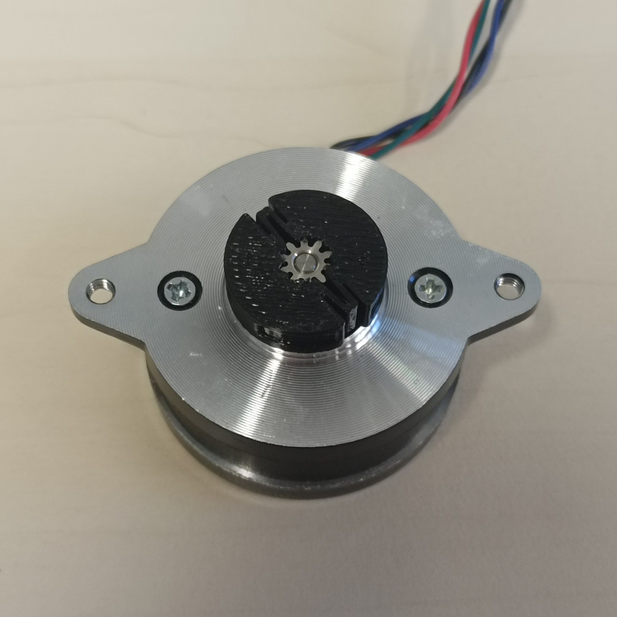
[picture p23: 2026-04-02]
images/instructions/step_03.jpg

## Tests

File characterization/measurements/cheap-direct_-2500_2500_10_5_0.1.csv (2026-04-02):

# file:
# name: cheap-direct_-2500_2500_10_5_0.1
# comment: ''
# date: '2024-11-08T15:32:46.895492'
# index_col: motor_input
# table_delim: "\t"
# user:
# motor_name: cheap-direct
# min_pos: -2500
# max_pos: 2500
# step: 10
# cycles: 5
# delay: 0.1
# meas_type: long
# input_units: null
# calibration:
# cam_position_um:
# - -801
# - -642
# - -446
# - -211
# - -61
# - 135
# - 328
# - 524
# - 709
# qpd_voltage_mV:
# - -6481.35
# - -5347.7
# - -3769.225
# - -1655.295
# - -204.915
# - 1661.76
# - 3415.0
# - 4999.98
# - 6362.025
# rescale_ref_um: 173
# rescale_ref_mV: 1790
# optical_lever_m: 0.75
# mirror_lever_m: 0.031
# compensated_backlash: 0
# input_to_translation: 1.52587890625e-08
# dev: {}
#
motor_input | qpd_voltage_mV
-2500 | -7654.0
-2490 | -9261.0
-2480 | -9293.0
-2470 | -9293.0
-2460 | -9279.0
-2450 | -9261.0
-2440 | -9266.0
-2430 | -9266.0
-2420 | -9258.0
-2410 | -9262.0
-2400 | -9259.75
-2390 | -9256.0
-2380 | -9256.0
-2370 | -9250.0
-2360 | -9250.0
-2350 | -9246.0
-2340 | -9225.0
-2330 | -9194.0
-2320 | -9194.0
-2310 | -9166.0
-2300 | -9124.0
-2290 | -9124.0
-2280 | -9088.0
-2270 | -9072.0
-2260 | -9067.0
-2250 | -9067.0
-2240 | -9022.0
-2230 | -8980.0
-2220 | -8952.4375
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

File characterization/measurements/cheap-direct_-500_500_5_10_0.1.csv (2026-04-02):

# file:
# name: cheap-direct_-500_500_5_10_0.1
# comment: ''
# date: '2024-11-08T15:02:20.124506'
# index_col: motor_input
# table_delim: "\t"
# user:
# motor_name: cheap-direct
# min_pos: -500
# max_pos: 500
# step: 5
# cycles: 10
# delay: 0.1
# meas_type: short
# input_units: null
# calibration:
# cam_position_um:
# - -801
# - -642
# - -446
# - -211
# - -61
# - 135
# - 328
# - 524
# - 709
# qpd_voltage_mV:
# - -6481.35
# - -5347.7
# - -3769.225
# - -1655.295
# - -204.915
# - 1661.76
# - 3415.0
# - 4999.98
# - 6362.025
# rescale_ref_um: 173
# rescale_ref_mV: 1790
# optical_lever_m: 0.75
# mirror_lever_m: 0.031
# compensated_backlash: 0
# input_to_translation: 1.52587890625e-08
# dev: {}
#
motor_input | qpd_voltage_mV
-500 | -175.0
-495 | -793.4375
-490 | -2154.0
-485 | -2145.0
-480 | -2145.0
-475 | -2134.0
-470 | -2134.0
-465 | -2097.0
-460 | -2099.375
-455 | -2116.0
-450 | -2104.0
-445 | -2104.0
-440 | -2093.0
-435 | -2097.625
-430 | -2130.0
-425 | -2124.0
-420 | -2124.0
-415 | -2081.0
-410 | -2081.0
-405 | -2086.0
-400 | -2092.0
-395 | -2110.0
-390 | -2116.0
-385 | -2116.0
-380 | -2071.0
-375 | -2071.0
-370 | -2037.0
-365 | -2034.25
-360 | -2033.0
-355 | -1976.0
-350 | -1976.0
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

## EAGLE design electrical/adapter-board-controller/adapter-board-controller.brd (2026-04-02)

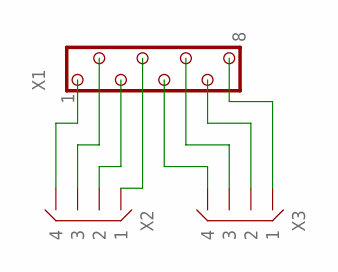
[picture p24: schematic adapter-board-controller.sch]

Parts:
X1: XS08-RJ45; XS08-2S-RJ45
X2, X3: X04; X04-SIL-MALE-VERT-L

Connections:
unnamed: X1.4, X2.1
unnamed: X1.3, X2.2
unnamed: X1.2, X2.3
unnamed: X1.1, X2.4
unnamed: X1.5, X3.4
unnamed: X1.6, X3.3
unnamed: X1.7, X3.2
unnamed: X1.8, X3.1

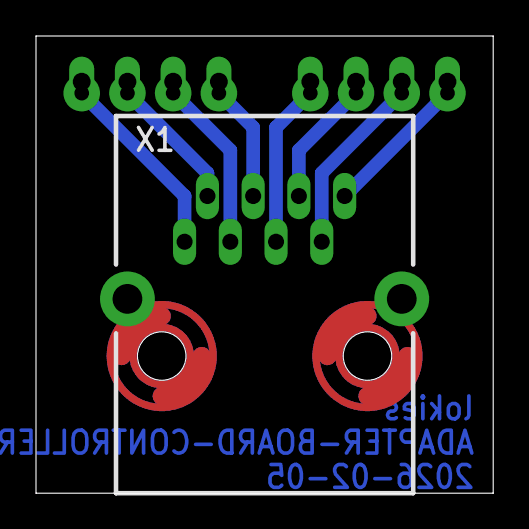
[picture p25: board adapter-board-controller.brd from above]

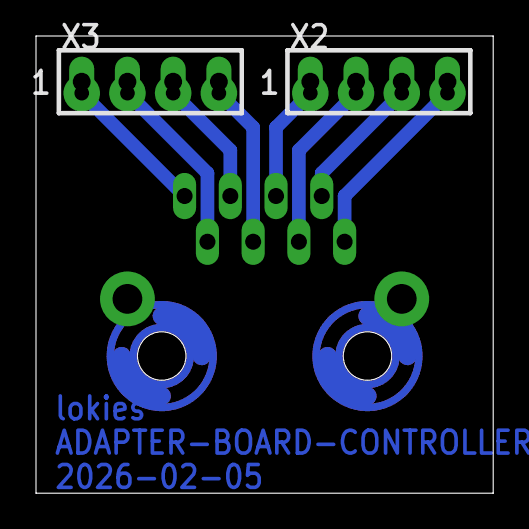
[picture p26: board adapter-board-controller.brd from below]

Board: 2 copper layers, 25.4 x 25.4 mm, 4 parts (3 on the bottom side), 8 nets.

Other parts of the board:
U$2: INFO-SMALL
